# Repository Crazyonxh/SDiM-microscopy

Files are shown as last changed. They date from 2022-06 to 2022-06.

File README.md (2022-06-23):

# SMART-microscopy
SMART is short for Spinning-disk Mesoscale ARbitrarily-shaped Surface imaging Technique, an open source framework adapted to different mesoscope and macrosopes.   

<p align="center">
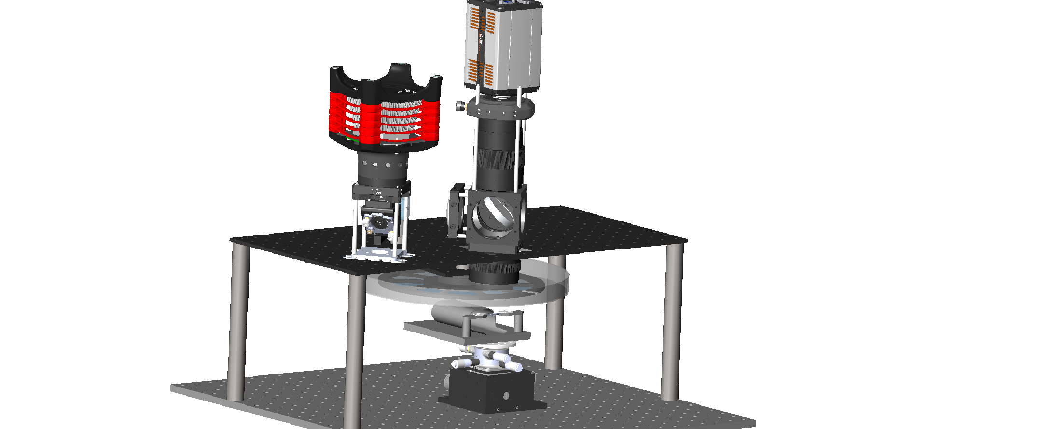
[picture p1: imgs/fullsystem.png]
hover text
  
</p>  

## Part list
### Spinning disk
* Disk, Customized from CNC, $50
* [Glass](https://item.taobao.com/item.htm?spm=a1z09.2.0.0.68c82e8dmFWsRe&id=536537929007&_u=8h1dbqsf77b), Thickness 0.16, 0.33, 0.55, 0.71, 0.88, 0.98, 1.33, 1.43, 1.5 mm, $100
* [IR detector](https://item.taobao.com/item.htm?spm=a230r.1.14.96.26a6262etMtMfx&id=565341450720&ns=1&abbucket=11#detail), $5
* [Rotation stage](https://item.taobao.com/item.htm?spm=a1z09.2.0.0.10132e8dwd0SDd&id=626679376761&_u=8h1dbqsd1cc), IM6824H  Lika Tech, $50
* [Motor drive](https://item.taobao.com/item.htm?spm=a1z09.2.0.0.10132e8dwd0SDd&id=628139875189&_u=8h1dbqs5019), 12-36V Lika Tech, $30
* [UV glue](https://detail.tmall.com/item.htm?spm=a230r.1.14.22.59be7edbpFXC4D&id=575402772223&ns=1&abbucket=11), 3218uv Valigoo, $1
* Tapes
### Selective illumination
* [Digital Micromirror Device](https://www.vialux.de/Website/PDF/ALP/Specification-V-Modules-Frame-Rates.pdf), V-7001 Vialux, ~$10000
* [LED](https://www.thorlabschina.cn/newgrouppage9.cfm?objectgroup_ID=8986), SOLIS-470C & DC20 Thorlabs, ~ $2,000
* [Relay lenses](https://www.thorlabs.com/thorProduct.cfm?partNumber=AC508-100-A), AC508-100-A Thorlabs, $100
### Synchronization
* [DAQ](https://www.ni.com/zh-cn/support/model.pxie-6363.html), USB-6363 NI, ~$3000
* Jump wire, $5
* PC, ~$2000
### Macroscope
* SLR lenses, Canon EF 50mm f/1.4 USM & MINILTA AF 100mm f/2.8, ~$200 for two second-hand lenses
* [Dichroic mirror](https://www.thorlabs.com/thorproduct.cfm?partnumber=DMLP505L), DMLP505L thorlabs, $400
* [Excitation filter](https://www.thorlabs.com/thorproduct.cfm?partnumber=FESH0500), $200
* [Emission filter](https://www.thorlabs.com/thorproduct.cfm?partnumber=MF525-39), $300
* [sCMOS detector](https://andor.oxinst.com/products/scmos-camera-series/zyla-5-5-scmos), Zyla 5.5 Andor, ~$20000

## Software Platform and code list
* Matlab R2020a  
`DMDCalibration/calculateTransform.m`calibrates the coordinates of DMD with sCMOS piexels.   
`surfaceDetection/generateDMDPattern.m` fits the arbitary surface and thereby generates target galss thickness.   
`DataAnalysis/NauralActivityAnalysis` generates the neural results.  
* Qt 5.14.2     
[`widefield/debug/widefild.exe`](https://figshare.com/s/6e0073230477a9e31000) is the executable program for SMART microscopy.
* Labview 2019 64 bit  
`acq/SMART.vi` is the main vi for SMART microscopy
* Python   
`boplot.py` plots the boxpolot figures with Seaborn.
* Solidworks 2020  
`SMART.stl` is the drawing of the spinning disk   

## Downloads
### System implementatoin
* [Andor SDK3.15](https://andor.oxinst.com/downloads/view/andor-sdk3-3.15.30084.0) 
* [Andor SDK3 Labview for sCMOS](https://andor.oxinst.com/assets/uploads/andor-support-resources/FAQ031.pdf)
* [Micromanager with Andor SDK3](https://micro-manager.org/Andor_SDK3) 
* [VIALUX-3P-ALP-4](https://www.ti.com/tool/VIALUX-3P-ALP-4) is the controller for DMD
### Data analysis
* [CNMF-E](https://github.com/zhoupc/CNMF_E)
* [circularGraph](https://ww2.mathworks.cn/matlabcentral/fileexchange/48576-circulargraph)
* [@msdanalyzer](https://ww2.mathworks.cn/matlabcentral/fileexchange/40692-mean-square-displacement-analysis-of-particles-trajectories)

## Step 1: Assembly of the spinning disk
1.	Our spinning disk is made of alumina. It is recommended to oxidize and paint the surface black. We attach a stick to the edge for synchronization
2.	The cover glass is cut by the manufacturer. We designed the glass to be a fan shape with an outer radius of 110 mm and an inner radius of 50 mm at an angle of 34 degrees. 
3.	Fix the glass plates to the disk with UV glue, and secured them with tape. The arrangement of the glasses is carefully designed to keep the center of mass on the axis.
4.	Attach the disk to the rotation stage, and connect the stage to the motor driver. 
5.	Fix the U-shaped IR detector close to the disk, so that the stick can trigger a digital edge.
6.	Put the whole system in a box for high-speed applications. 

## Step 2: Assembly of the illumination
1.	Our illumination light path is identical to the conventional structured illumination light path. But we use regional illumination so it has a lower requirement for optical design
2.	First relay the illumination LED to the DMD so that a uniform pattern is formed, as instructed by the manufacturer. 
3.	Relay the DMD through the doublet lens and objective the specimen.
4.	Drop some fluorescence solution on the slide and cover it with a cover glass.
5.	Generate some patterns (points) on the DMD, and record the image on the camera.
6.	Align the coordination on the camera to the coordinate of DMD (in Matlab control point select tool), with images from the camera and the DMD.

## Step 3: Signal synchronization
1.	We develop two modes for synchronization: a master mode and a slave mode. In the master mode, the position of the spinning disk works as the trigger source, while the DMD and camera follow the time sequence of the disk. However, for systems in which we cannot control the trigger of cameras, we use a slave mode in which the disk and DMD follow the timing of the camera.
2.	In the master mode, we first set the voltage of the motor drive to control the speed of the disk. At the start of each cycle, the stick on the disk triggers a signal on the IR detector and sends the message to the counter on DAQ. Then a digital trigger signal is sent to initiate the start of camera exposure and another trigger signal is sent to the DMD to start its display.
3.	The exposure time of the camera is set to be equal to the duration of the rotation.
4.	The display time of the DMD is set to equal to the time for each cover glass. 
5.	If there are more than more cover glasses in the field of view, the LED is turned off.
6.	In the slave mode, everything is the same except that a PID process is used to set the control voltage on the motor, so that the period of rotation is equal to the exposure time of the camera. 
## Step 4: Surface detection
1.	On an initial scan, the disk rotates at a low speed and the camera takes one image at each cover glass. 
2.	The images are rearranged according to the order of the glass thickness. 
3.	Apply algorithms to extract the features. For example, to detect the position of neurons, we first use standard derivation to the time sequence, then threshold the image to make it binary and apply morphological algorithms to extract the connected regions in the image. Finally, we sort the regions by parameters such as areas and eccentricity.
4.	We fit the shape of our surface by assuming the surface is continuous in 3D space. The shape of the surfaces can be set to polynomial or any smooth surface.
5.	Discrete the surface into 10 heights, and make 10 binary masks accordingly. 

## Step 5: Image acquisition
1.	Apply the map-table in Step 2.6 to the illumination pattern, and set the DMD.
2.	For Labview detection, follow this [manual](./Labveiw/readme_labview.md). For QT detection, download this [zip file](https://figshare.com/s/6e0073230477a9e31000).

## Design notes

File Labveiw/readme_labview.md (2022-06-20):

## Requirements

* NI Labview 2019 64bit 
(https://www.ni.com/en-us/support/downloads/software-products/download.labview.html#329483)
* NI DAQmx 
(https://www.ni.com/en-us/support/downloads/drivers/download.ni-daqmx.html#382067)
* NI Vision Acquisition
(https://www.ni.com/en-us/support/downloads/drivers/download.vision-acquisition-software.html#367318)
* Andor LabView SDK3
(https://andor.oxinst.com/downloads/view/sdk3-for-labview-3.15.30065.0)

    We use version 3.15.30000.0, which is no longer exist on the website.
* DMD driver ALP 4.3
(https://www.vialux.de/en/download.html)

    We use ALP43_install-R706.exe, which is no longer exist on the website. Our program may be not compatible with the newer version ALP43_install-R765.exe.

    To use API in labview, import the library by 'Tools->Import->Shared library(.dll)' after installing the driver.  (https://knowledge.ni.com/KnowledgeArticleDetails?id=kA00Z0000019Ls1SAE&l=en-GB)

## Wiring Guide

* Dev1/ao1 is used to control the speed of the rotary stage.

* Dev1/PFI9 links to the IR detector, which triggers the following digital output task and measures the speed of rotary stage using Dev1/ctr0.

* Dev1/port0/line0:2 link to the external trigger of DMD (line0), camera (line1) and LED (line2).

## Software Guide

### 1. Use 'Free Run' mode to test rotary stage, camera, DMD and LED.
* Enter a voltage at 'rotary voltage', the stage should start to move. 

    Click the button beside 'rotary voltage', 'rps' and 'T(ms)' should show the speed.

    
* Click 'DMD' and 'LED' button to see if they can be controlled.

    

* 'open camera'->'apply settings'->'live'->'stop live' to test the sCMOS camera. 
    
    Use 'save images' to acquire and save some images. (If the camera temperature is high, turn on 'SensorCooling' in micro-manager)

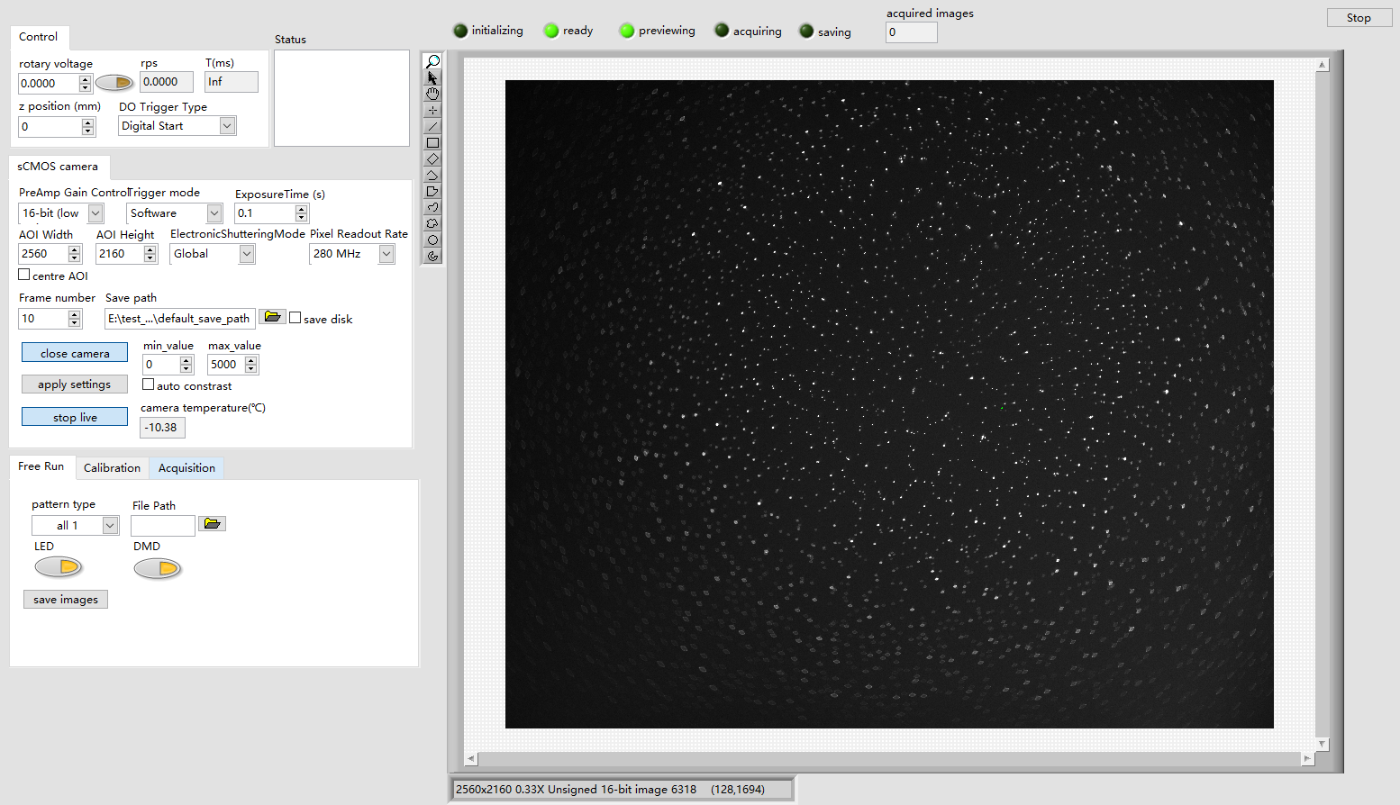
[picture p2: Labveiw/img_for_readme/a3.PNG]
    

### 2. Use 'Calibration' mode to get images for surface detection.
* Set 'signal time' to a number that is a little smaller than 'T(ms)'. Set 'Frame number to 1 for normal sample, to 50 for neurons. After 'apply settings' -> 'start cali', there will be some images in the folder '.\default_image_path\default_save_path\'. 

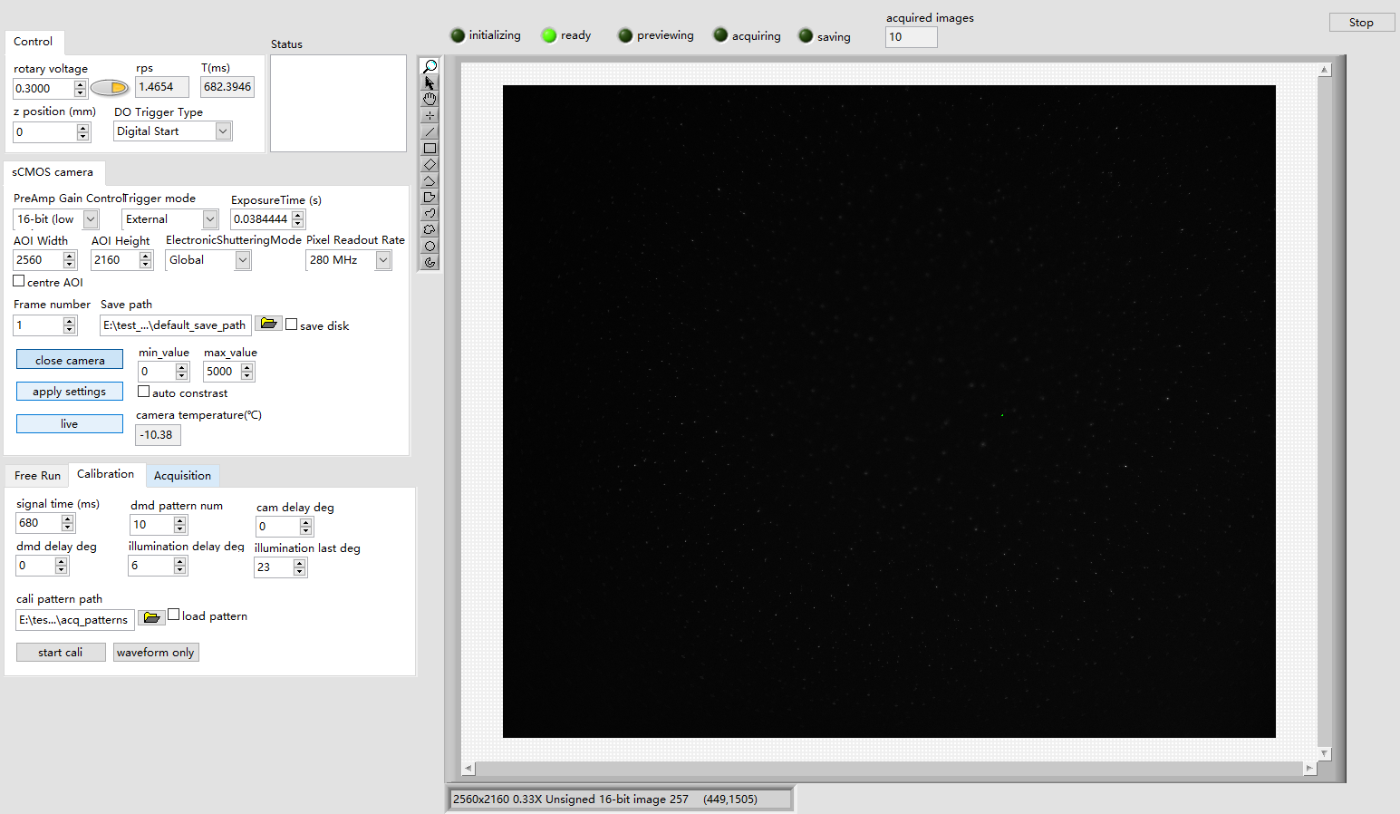
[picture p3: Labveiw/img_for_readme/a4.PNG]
    

### 3. Surface detection
* Fit the surface with algorithms or manually. We put beads on a lens and use it as our sample here.

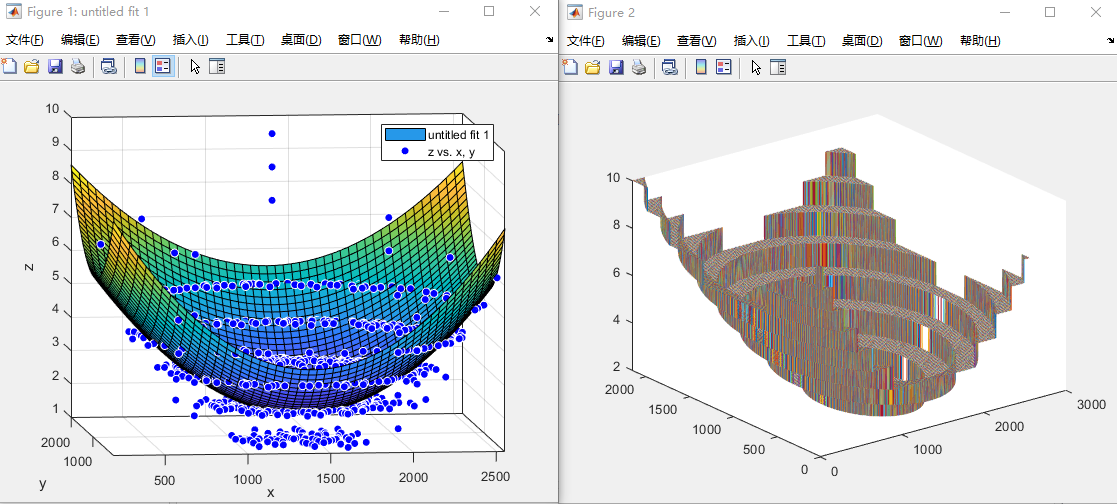
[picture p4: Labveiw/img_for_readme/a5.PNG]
    

### 4. Use 'Acquisition' mode to image the surface
* After surface detection, there should be a folder containing DMD patterns. Set 'acq pattern path' to this folder. 'apply settings'->'start acq', there will be some images in the '.\default_image_path\default_save_path\'. 

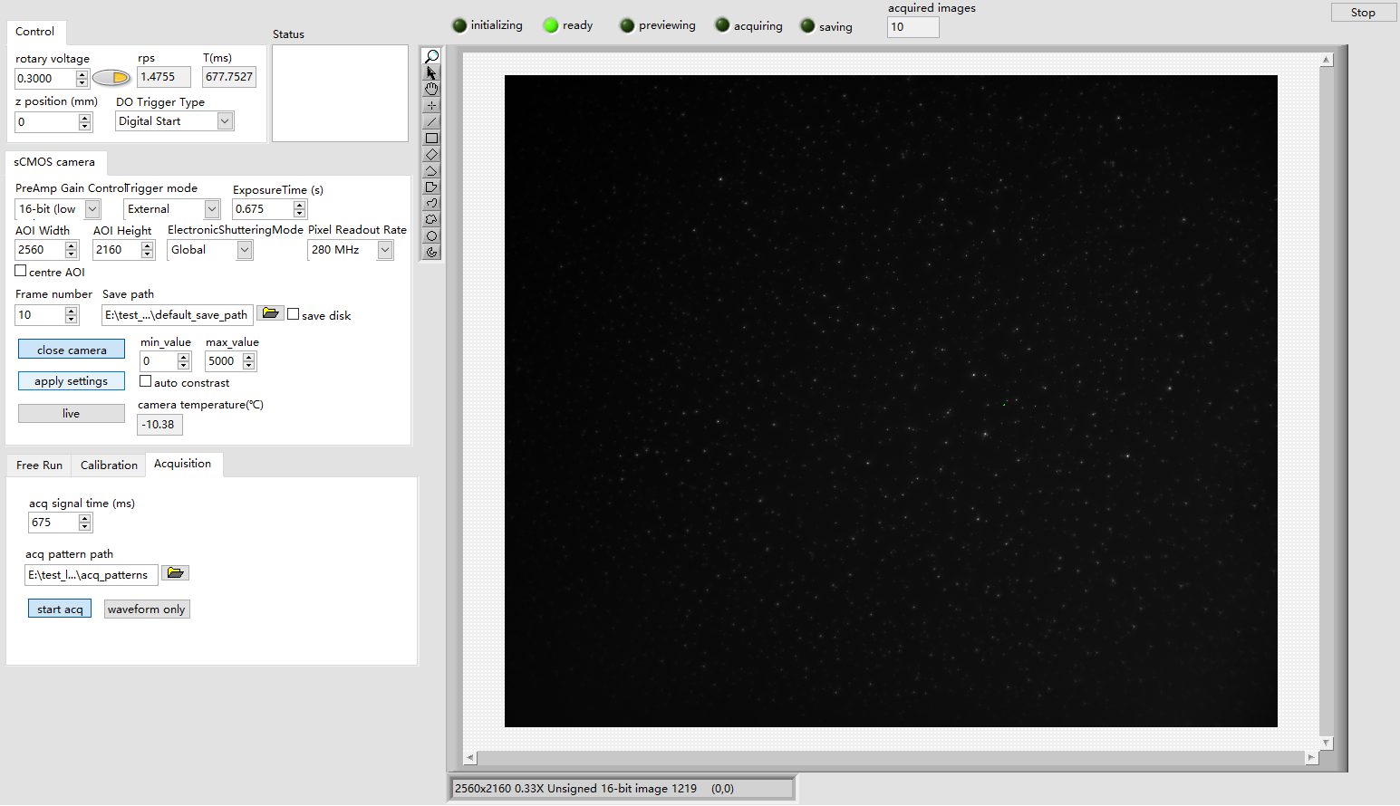
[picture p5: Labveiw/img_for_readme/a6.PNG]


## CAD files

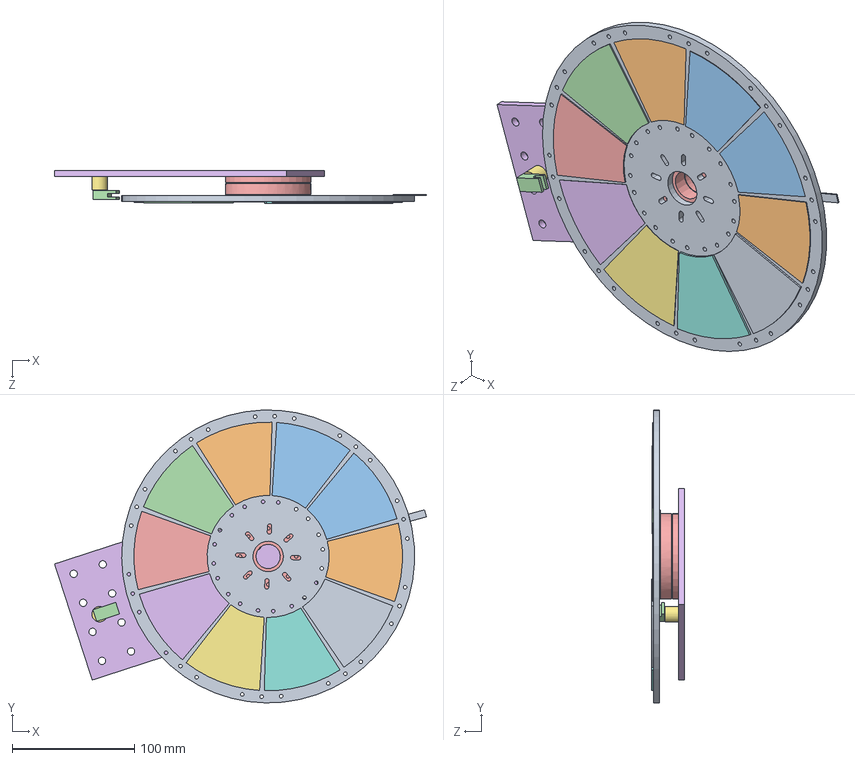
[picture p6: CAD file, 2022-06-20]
SMART drawings/disk_assembl.SLDASM
304.7 x 239.9 x 27.0 mm
disk2
glass1_8
glass0_53
glass0_98
glass0_88
glass0_16
glass0_33
glass1_50
glass1_33
glass0_71
glass0
IRDetector
stage
baseplate
postForIR

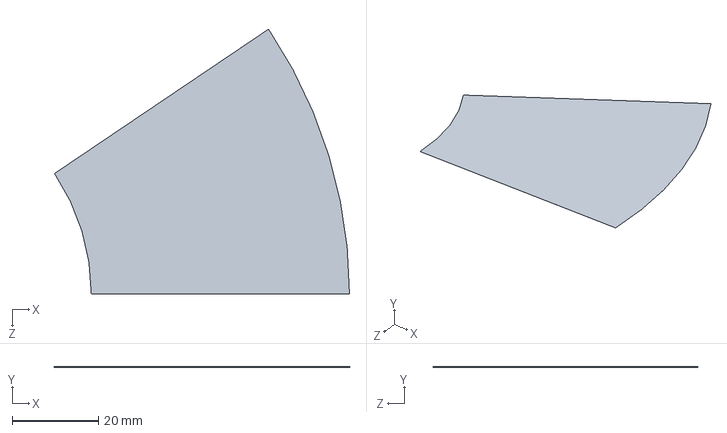
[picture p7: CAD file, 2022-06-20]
SMART drawings/glass0.SLDPRT
68.5 x 0.001 x 61.5 mm

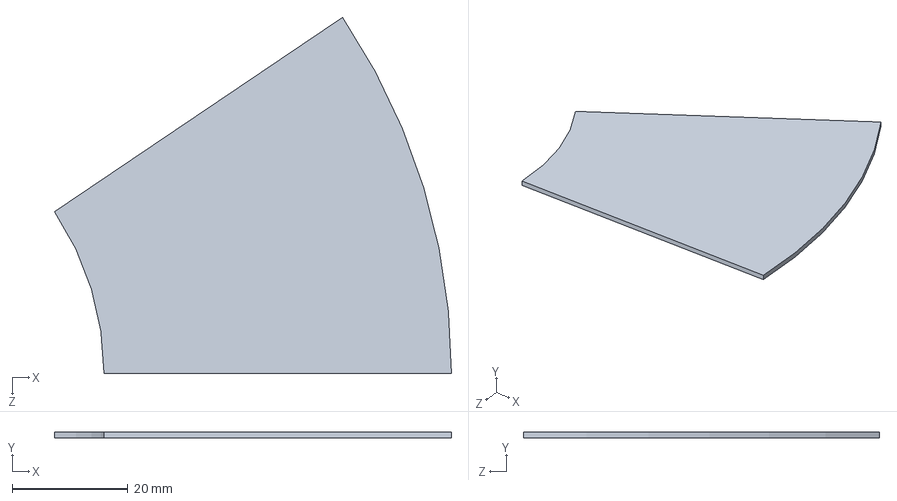
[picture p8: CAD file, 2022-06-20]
SMART drawings/glass0_98.SLDPRT
68.5 x 0.98 x 61.5 mm

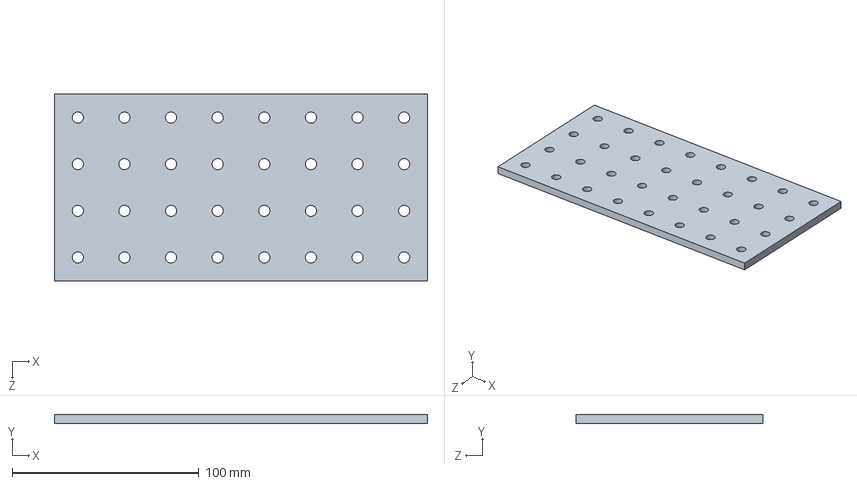
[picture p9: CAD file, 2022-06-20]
SMART drawings/baseplate.SLDPRT
200.0 x 5.00 x 100.0 mm

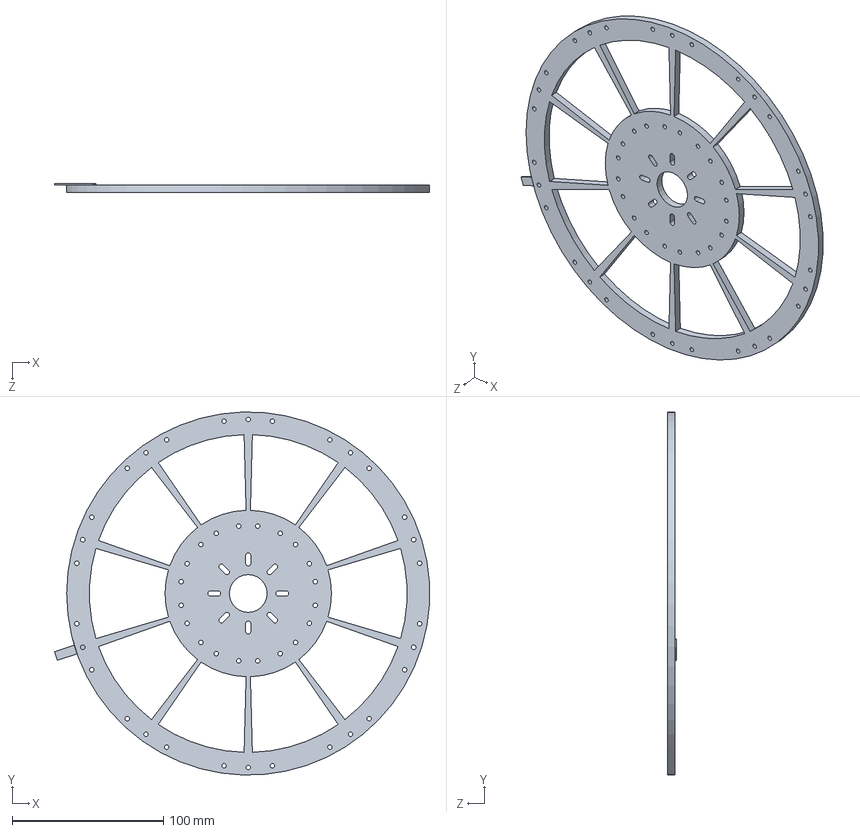
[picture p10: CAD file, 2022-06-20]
SMART drawings/disk2.SLDPRT
247.8 x 239.9 x 6.00 mm

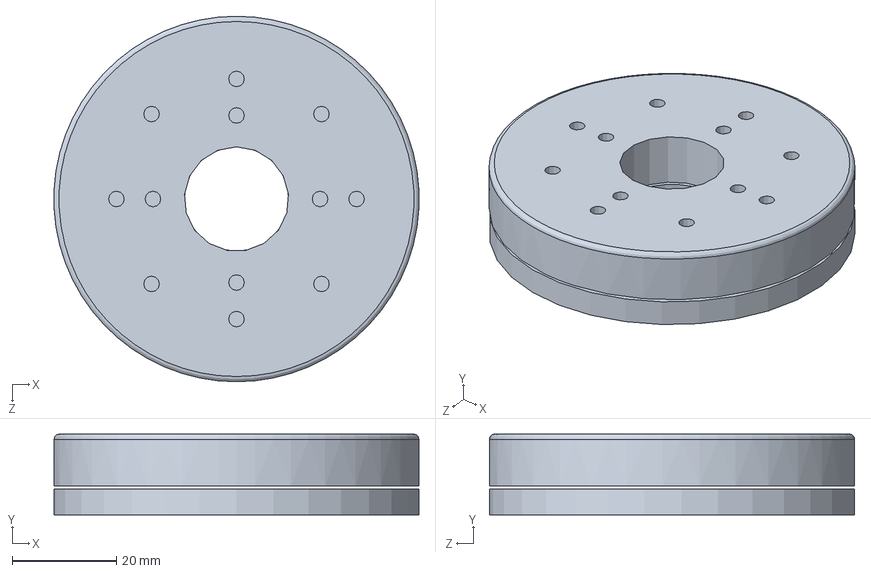
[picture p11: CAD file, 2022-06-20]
SMART drawings/stage.SLDPRT
69.9 x 15.5 x 70.0 mm

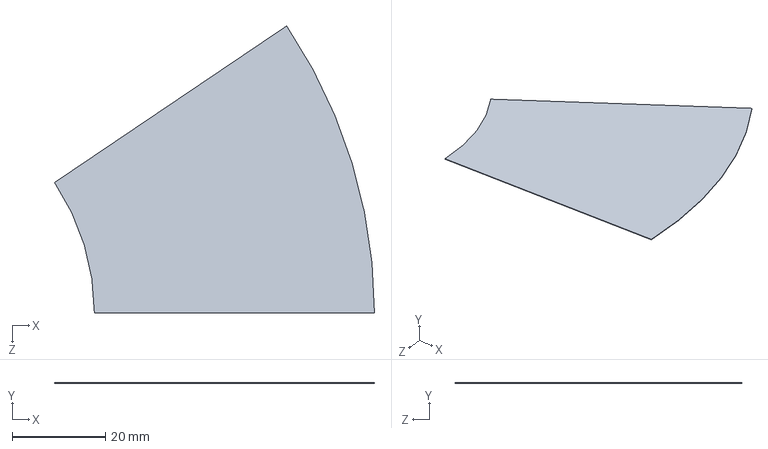
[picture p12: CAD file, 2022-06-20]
SMART drawings/glass0_16.SLDPRT
68.5 x 0.13 x 61.5 mm

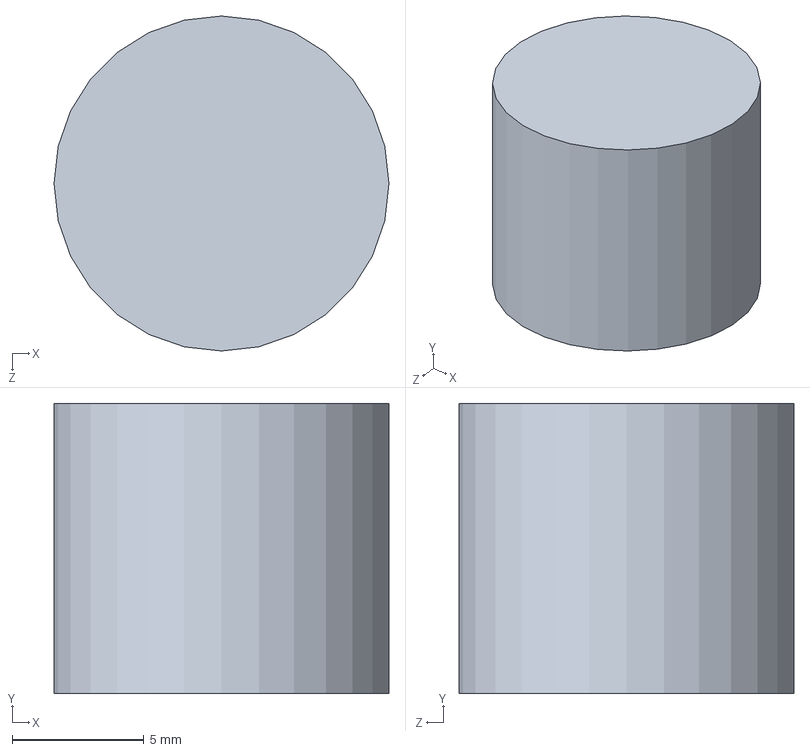
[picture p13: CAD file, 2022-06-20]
SMART drawings/postForIR.SLDPRT
12.7 x 11.0 x 12.7 mm

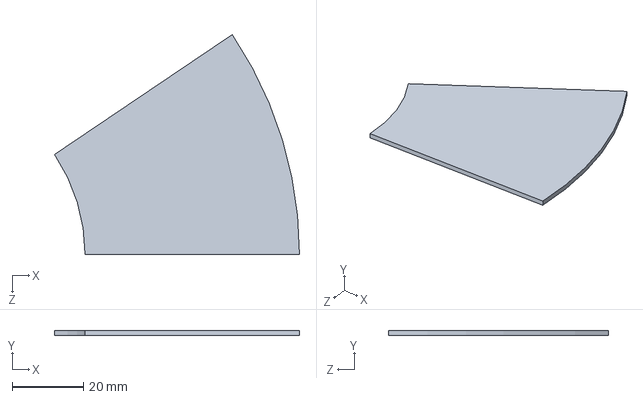
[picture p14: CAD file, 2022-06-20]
SMART drawings/glass1_33.SLDPRT
68.5 x 1.33 x 61.5 mm

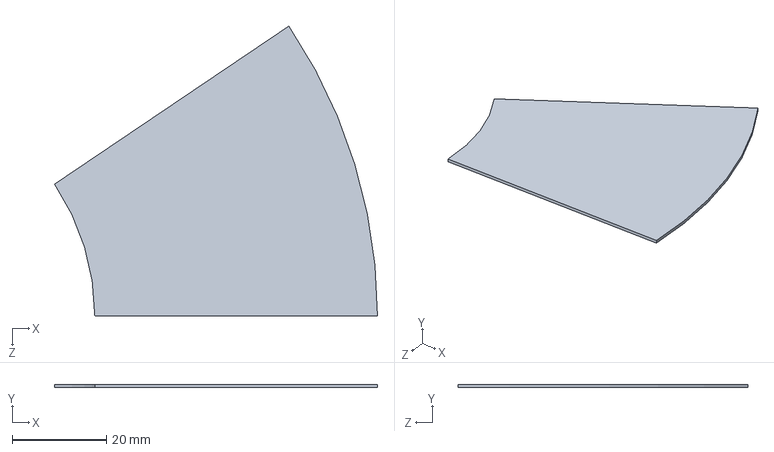
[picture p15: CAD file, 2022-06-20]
SMART drawings/glass0_71.SLDPRT
68.5 x 0.71 x 61.5 mm

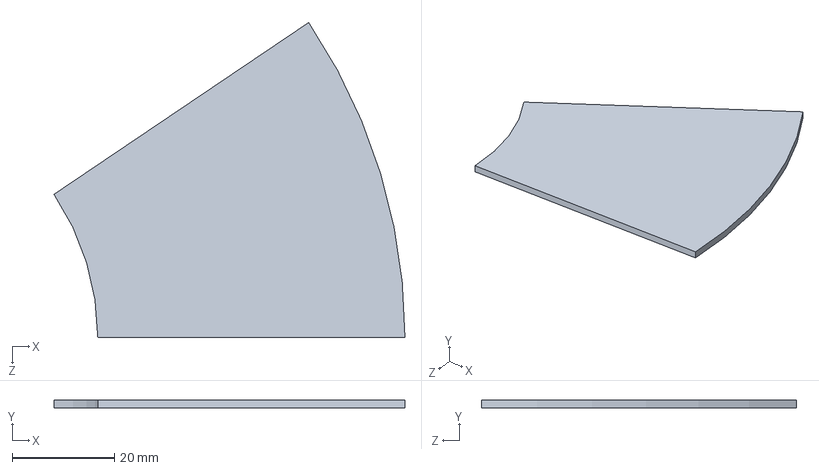
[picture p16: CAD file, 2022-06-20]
SMART drawings/glass1_50.SLDPRT
68.5 x 1.50 x 61.5 mm

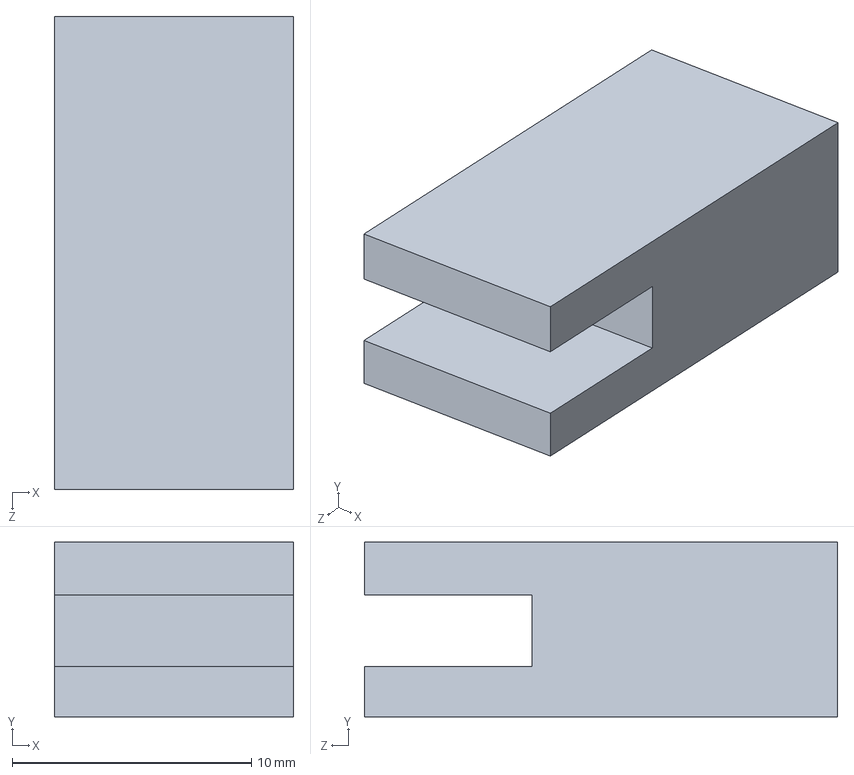
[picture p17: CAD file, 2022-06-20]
SMART drawings/IRDetector.SLDPRT
10.0 x 7.29 x 19.8 mm

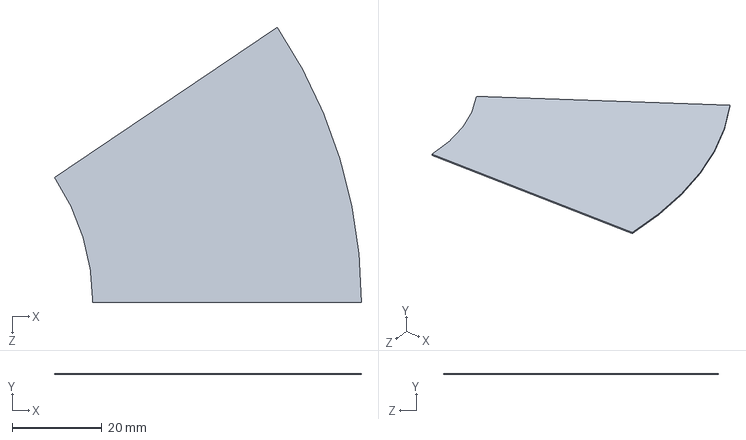
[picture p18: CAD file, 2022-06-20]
SMART drawings/glass0_33.SLDPRT
68.5 x 0.33 x 61.5 mm

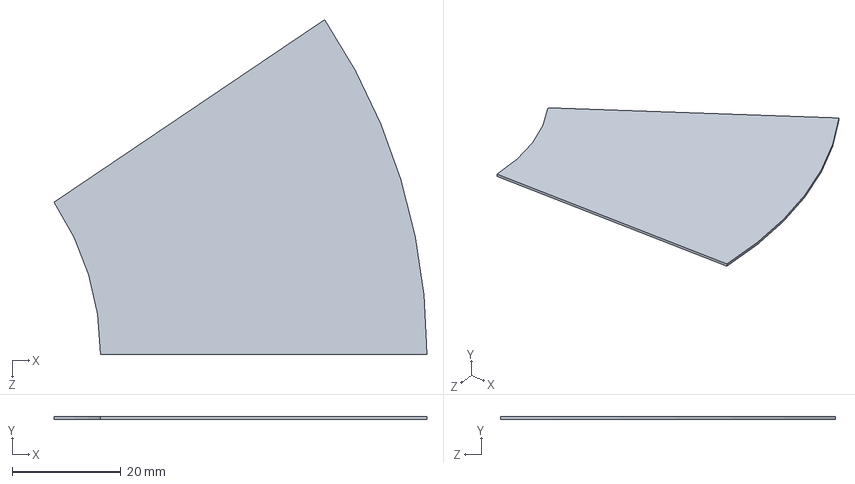
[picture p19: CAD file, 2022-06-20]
SMART drawings/glass0_53.SLDPRT
68.5 x 0.53 x 61.5 mm

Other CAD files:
SMART drawings/glass1_8.SLDPRT
SMART drawings/glass0_88.SLDPRT

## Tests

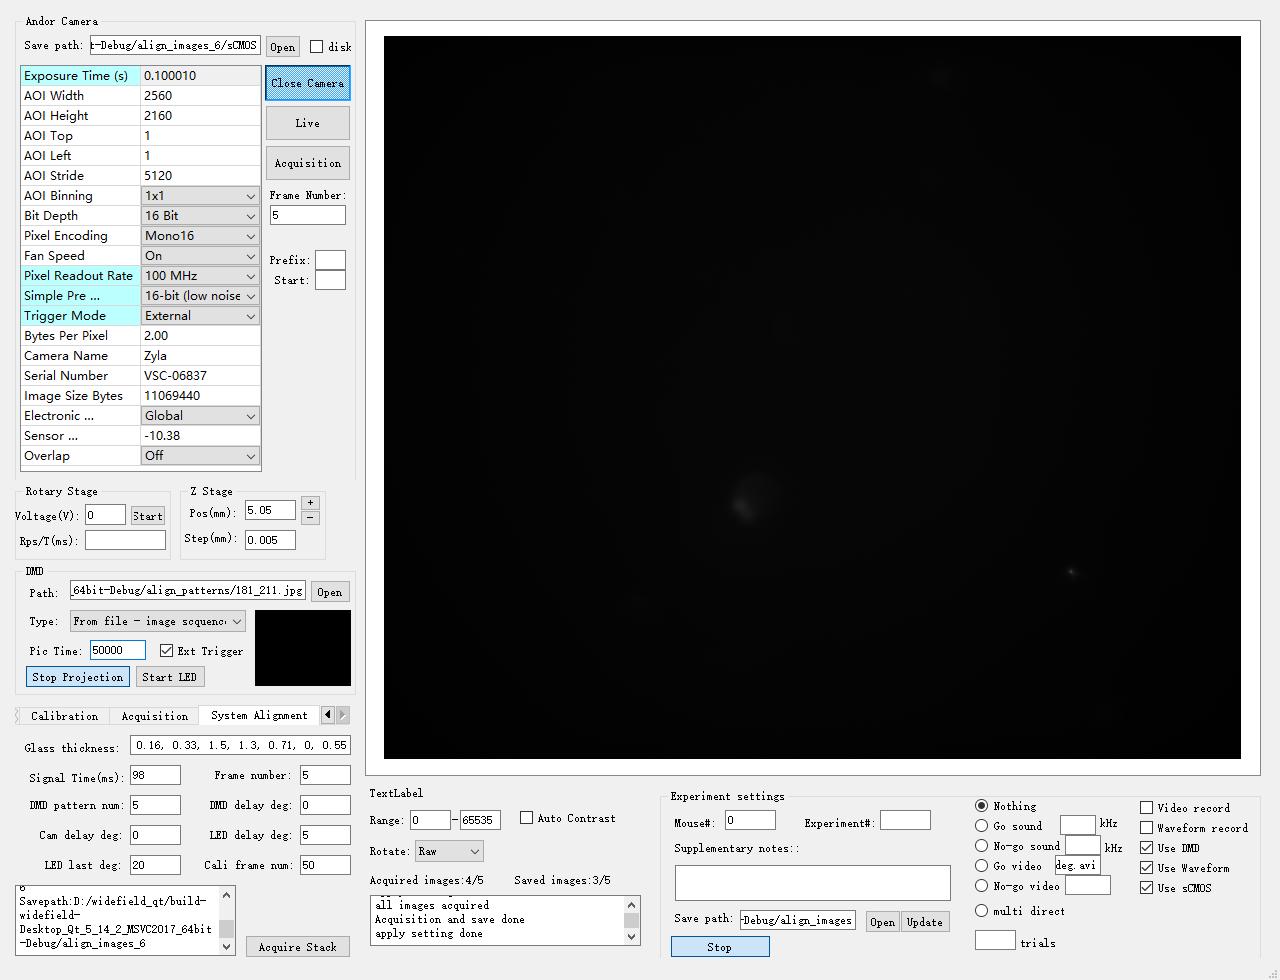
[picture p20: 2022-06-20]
DMDCalibration/align_images_6/parameter.jpg
